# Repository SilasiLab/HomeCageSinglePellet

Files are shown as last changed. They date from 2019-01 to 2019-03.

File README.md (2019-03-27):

# **Overview**:

This system allows the user to host up to 5 mice in their home environment and automatically administer the single pellet reaching test to those animals. The system can run unsupervised and continuously for weeks at a time, allowing all 5 mice to perform an unlimited number of single pellet trials at their leisure. 

The design allows a single mouse at a time to enter the reaching tube. Upon entry, the animal’s RFID tag will be read, and if authenticated, a session will start for that animal. A session is defined as everything that happens from the time an animal enters the reaching tube to when they leave the tube. At the start of a session, the animal’s profile will be read and the task difficulty will be automatically adjusted by moving the pellet presentation arm to the appropriate distance away from the reaching tube. After the difficulty is set, pellets will begin being presented with either the left or right presentation arm, depending on which arm is specified in the mouse’s profile. Pellets will continue to be presented periodically until the mouse leaves the tube, at which point the session will end. Video and other data is recorded for the duration of each session. At session end, all the data for the session is saved in an organized way. 

# **Dependencies:**
* Ubuntu v16.04 LTS: Kernel version 4.4.19-35 or later
* Python v3.5.2
	* pySerial	
	* numpy
	* OpenCV v3.4.x
	* tkinter 
	* matplotlib
	* Pillow
	* tqdm
* Flir Spinnaker SDK v1.10.31
	* libavcodec-ffmpeg56
	* libavformat-ffmpeg56
	* libswscale-ffmpeg3
	* libswresample-ffmpeg1
	* libavutil-ffmpeg54
	* libgtkmm-2.4-dev
	* libusb-1.0-0
	
	Note: The Spinnaker dependencies are installed via official Spinnaker SDK install script.
* Arduino IDE v1.8.5

# **Software Installation:**
1. Install Ubuntu 16.04 LTS on your machine.
2. Install Anaconda. (https://www.anaconda.com/distribution/)
3. Install the Flir Spinnaker SDK v1.10.31 **INSERT GOOGLE DRIVE LINK TO SPINNAKER SDK HERE**
4. Install Arduino IDE v1.8.5. (https://www.arduino.cc/en/Main/Software)
5. Install OpenCV for C++.
	- `sudo apt-get install build-essential cmake git libgtk2.0-dev pkg-config libavcodec-dev libavformat-dev libswscale-dev`
	- `sudo apt-get install libjpeg-dev libpng-dev libtiff5-dev libjasper-dev libdc1394-22-dev libeigen3-dev libtheora-dev 			libvorbis-dev libxvidcore-dev libx264-dev sphinx-common libtbb-dev yasm libfaac-dev libopencore-amrnb-dev 			libopencore-amrwb-dev libopenexr-dev libgstreamer-plugins-base1.0-dev libavutil-dev libavfilter-dev 				libavresample-dev`
	- `sudo -s`
	- `cd /opt`
	- Download OpenCV source from https://github.com/opencv/opencv/releases/tag/3.4.4 and unpack it into /opt
	- Download OpenCV_contrib source from https://github.com/opencv/opencv_contrib/releases/3.4.4 and unpack it into /opt
	- `cd opencv`
	- `mkdir release`
	- `cd release`
	- `cmake -D BUILD_TIFF=ON -D WITH_CUDA=OFF -D ENABLE_AVX=OFF -D WITH_OPENGL=OFF -D WITH_OPENCL=OFF -D WITH_IPP=OFF -D 			WITH_TBB=ON -D BUILD_TBB=ON -D WITH_EIGEN=OFF -D WITH_V4L=OFF -D WITH_VTK=OFF -D BUILD_TESTS=OFF -D 				BUILD_PERF_TESTS=OFF -D CMAKE_BUILD_TYPE=RELEASE -D CMAKE_INSTALL_PREFIX=/usr/local -D 						OPENCV_EXTRA_MODULES_PATH=/opt/opencv_contrib/modules /opt/opencv/`
	- `make j4`
	- `make install`
	- `ldconfig`
	- `exit`
	- `cd`
	- `pkg-config --modversion opencv`
	- If everything worked correctly, output should read "3.4.4".
	
5. Create and configure a virtual environment for installing the HomeCageSinglePellet code.
	- `conda create -n <yourenvname> python=3.5.2 anaconda`
	- `conda activate <yourenvname>`
	- `conda install -c conda-forge opencv=3.4.4`
	- `conda install -c anaconda numpy`
	- `conda install -c anaconda pyserial`
	- `conda install -c anaconda tk`
	- `conda install -c conda-forge matplotlib`
	- `conda install tqdm`
	- `conda install Pillow`

6. Download the HCSP source code from https://github.com/SilasiLab/HomeCageSinglePellet and unpack it.
7. Optional (Only if you want to use the analysis features): Install Deeplabcut using the Anaconda based pip installation method. (https://github.com/AlexEMG/DeepLabCut/blob/master/docs/installation.md)
8. Optional (Only if you want to use the anaylsis features): Move the file `HomeCageSinglePellet/src/analysis/HCSP_analyze.py` into `~/.conda/envs/DLC2/lib/python3.6/site-packages/deeplabcut` (Where DLC2 is the name of the anaconda virtual environment where you installed Deeplabcut).
9. Optional (Only if you want to use the anaylsis features): Download our pretrained DLC2 network for automatically extracting reach attempts from your videos. **INSERT GOOGLE DRIVE LINK TO NETWORK HERE**
8. Done!

# **Assembly:**

### **Prerequisites:**

1. Obtain all the parts listed in `HomeCageSinglePellet/resources/partsList.xls`
2. Have the PCB `HomeCageSinglePellet/resources/PCB/nano.brd` manufactured (Find a manufacturer, send them the .brd file using
whatever process they use for upload, wait for it in the mail).
3. 3D print all the .stl files contained in `HomeCageSinglePellet/resources/CAD/STL/`

### **Attach headers and components to the PCB**

1. Attach female headers for the Arduino onto the PCB. Attach male headers onto the CAMTRIG, MSZ, SERVO1, SERVO2, RFID and
IRBREAK holes on the PCB.
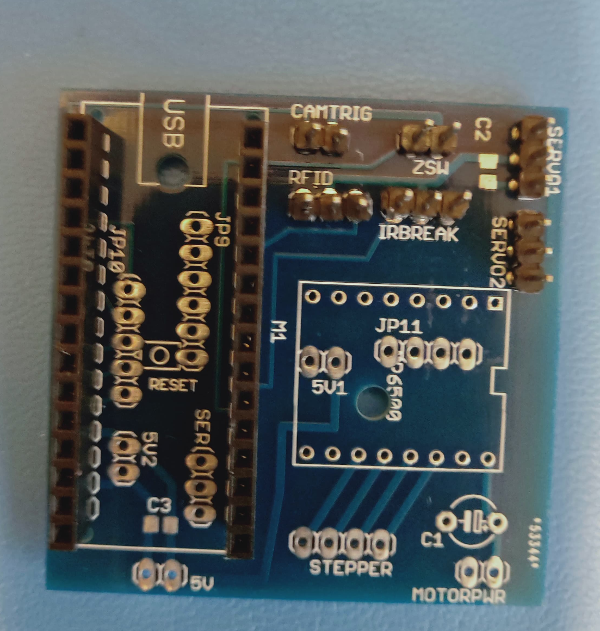
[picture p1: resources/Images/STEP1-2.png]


2. Solder the stepper driver to the PCB in the orientation shown in the picture. (Note that the holes on 
the PCB are spaced too far apart for the stepper driver pins). To address this we bend the pins of the driver to fit. You'll 
need to do this until someone gets around to fixing the PCB layout.

	
3. Solder the capacitor across C1 as shown in the picture. (TODO: INSERT PICTURE)

### **Install the voltage regulator and power connectors**

4. Voltage regulator output must be set to 5V by turning the small screw on the blue pot. This is done my powering the device with 12V and recording the output with multimeter while adjusting the pot screw.
Attach 6 leads to the voltage regulator:
	- 2 Leads to the positive input pad.
	- 2 leads to the negative input pad.
	- 1 lead to the positive output pad.
	- 1 lead to the negative output pad.


	
5. Short the neutral and ground leads on the circular power connectors by soldering a small wire across them.


6. Line up the voltage regulator in the box and drill holes through the box where you want to mount the regulator.


7. Screw one of the circular power connectors into the bottom hole.


8. Solder one of the negative input leads you attached to the voltage regulator in step 1 onto the negative lead of the 
power connector you screwed in in step 4.


9. Solder one of the positive input leads you attached to the voltage regulator in step 1 onto the positive lead of the
power connector you screwed in in step 4. 


10. Place the PCB into the box and drill holes into the box where the mount holes on the PCB line up. 
Then mount the PCB with some bolts. Metal bolts are fine, they won't touch anything that will be a problem. 
Use nylon washers if you're nervous.


11. Solder the remaining positive input power lead that you attached to the voltage regulator in 
step 5 to the positive MOTORPWR pad on the PCB.


12. Solder the remaining negative input power lead that you attached to the voltage regulator in 
step 5 to the negative MOTORPWR pad on the PCB.
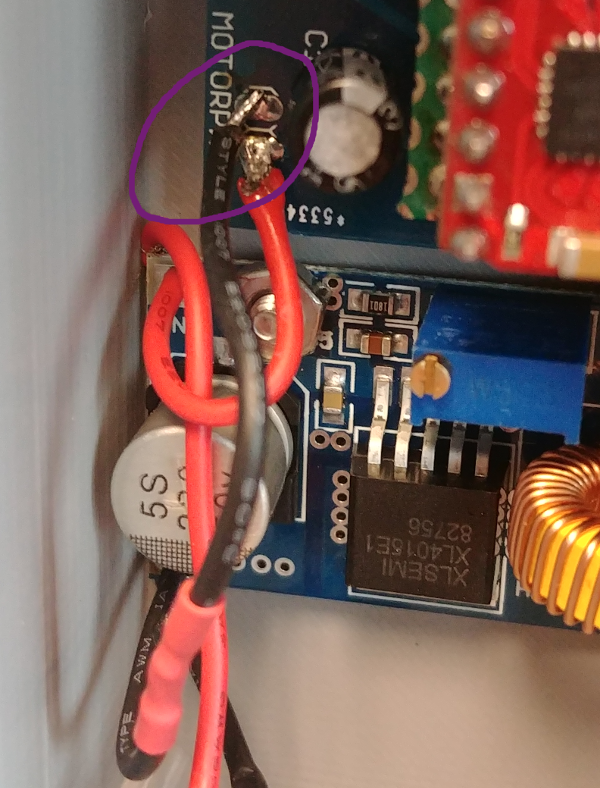
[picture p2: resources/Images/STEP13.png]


13. Screw in the second circular power connector to the remaining hole in the box. Solder a wire from the negative lead of the
second power connector to the negative lead of the first power connctor. Solder a wire from the positive lead of the second power
connector to the positive lead of the first power connector.
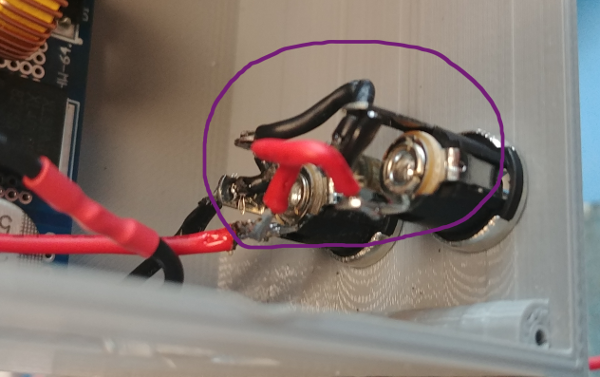
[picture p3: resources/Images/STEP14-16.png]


### **Assemble the pellet delivery system and mouse tube**

14. Line the hopper rail piece up on the baseplate and screw in the 4 screws that hold it in place.


15. Attach the stepper motor as shown in the picture. Attach the coupler to the shaft of the motor. **Note:** For the steps involving the stepper motor, coupler and coupling screw; We don't yet have a design that uses standard parts. We currently take the screw detailed in the parts list and cut it and the stepper motor shaft to the correct lenght. **INSERT CORRECT LENGTH OF STEPPER MOTOR SHAFT AND COUPLING SCREW HERE.**

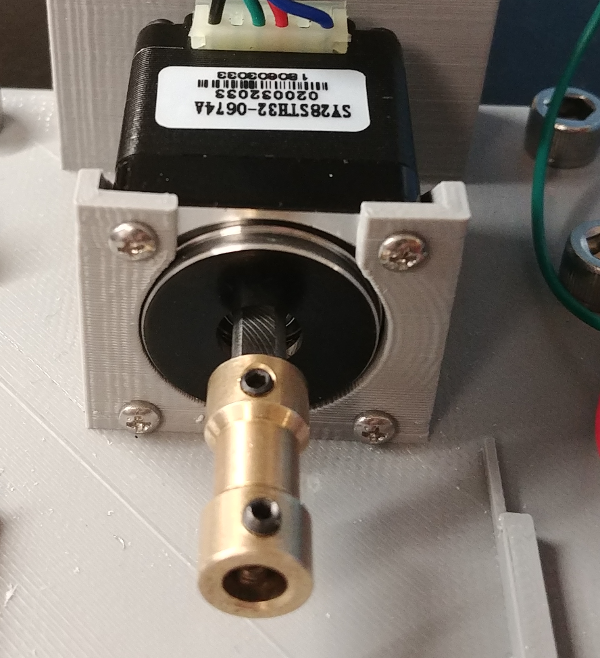
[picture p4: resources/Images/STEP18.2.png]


16. Attach the screw to the stepper coupler. Slide the hopper onto the rails and insert the nut into the slot where the stepper coupler screw will go. Then thread the shaft coming out of the coupler into the nut. 
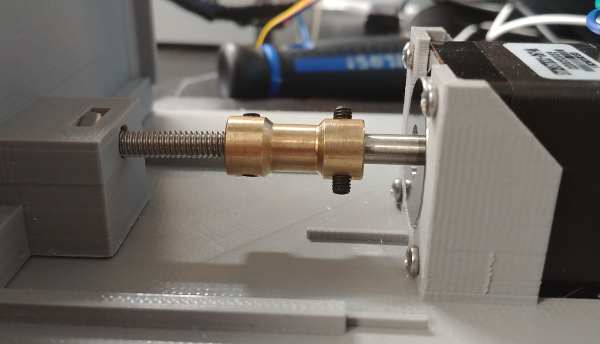
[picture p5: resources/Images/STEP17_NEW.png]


17. Rotate the stepper coupler until the screw is all the way into the hopper nut. Solder two leads to the microswitch,
one each on the left and right prongs coming out of the switch. Use superglue to glue the microswitch down so it will be pressed
when the hopper reaches it's closest point to the motor. 
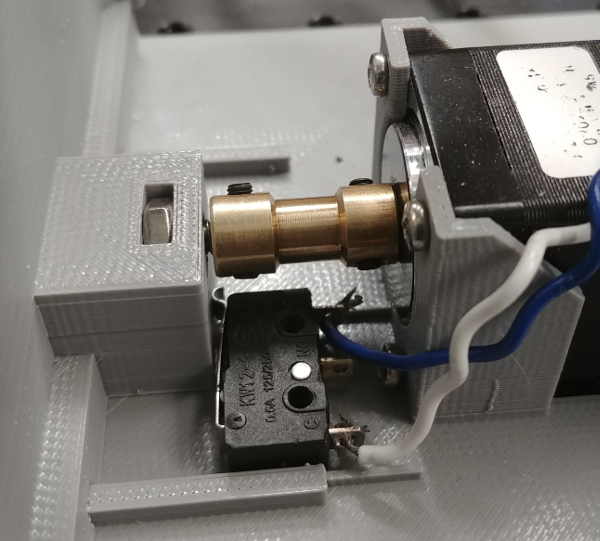
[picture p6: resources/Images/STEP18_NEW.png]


18. Attach both front surface mirrors to the mirror mount piece with double sided tape.


19. Slide the front-wall/mirror holder piece over the end of the acrylic tube.


20. Use your favorite adhesive to attach the IR-Breaker to the IR-Breaker holder.
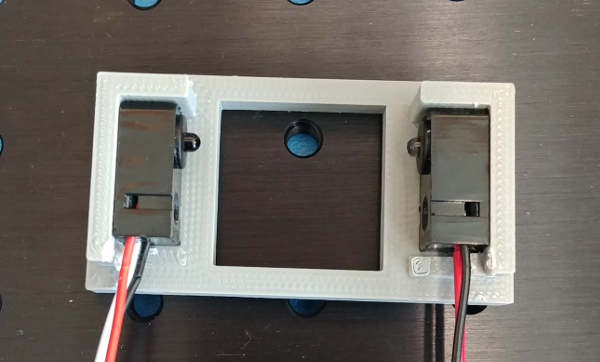
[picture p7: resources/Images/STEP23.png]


21. Slide the IR-Breaker holder over the tube so that the beam runs across the bottom of the tube 
(Where the mice feet will be).
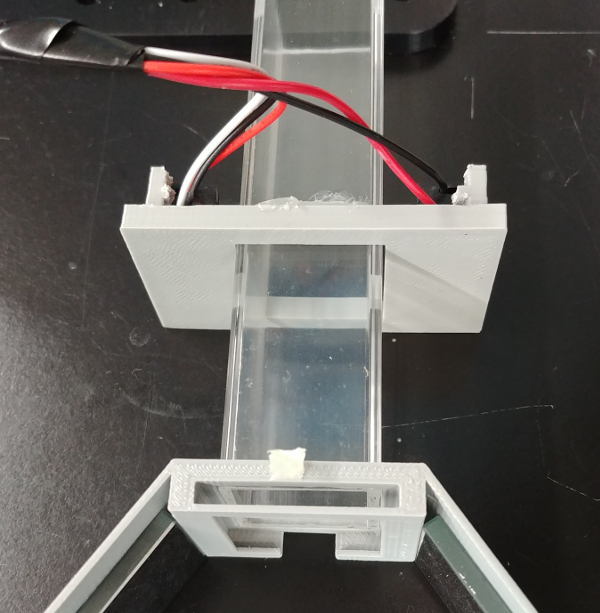
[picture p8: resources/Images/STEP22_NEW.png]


22. Hotglue the RFID reader to the acrylic tube as shown.(Note: Push the IR-Breaker holder up against the RFID module so that 
it's sandwiched between the IR-Breaker holder and the front-wall/mirror holder, and hot glue it all in place).


23. Slot the assembled acrylic tube into the square hole on the rail baseplate mount as shown.


24. Line up both servos as shown in the picture. Rotate the servo splines as far as they will go in the 
directions shown in the picture.


25. Use an allen key to insert the set screws into the tips of the hopper arms.
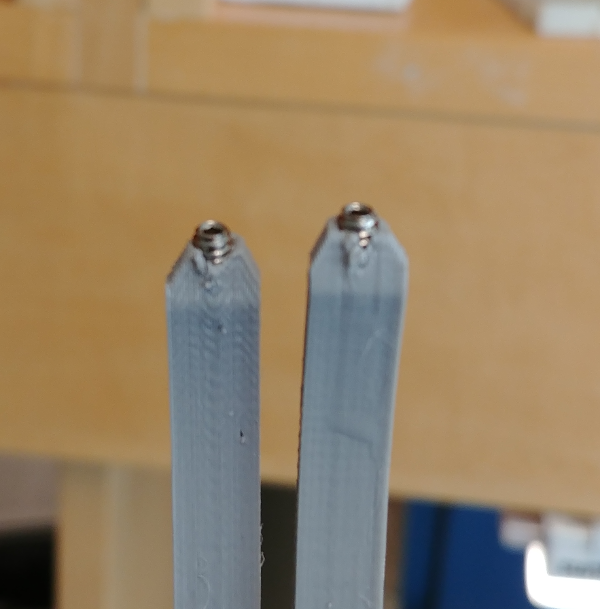
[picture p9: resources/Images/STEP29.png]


26. Attach the hopper arms to the servo spline as shown in the picture. (Note: This is why we 
rotated the servo spline as far as possible in step 28, so that you can set the maximum retraction 
point of the hopper arms by attaching them how you like).


27. Line the servos with attached hopper arms up as shown in the picture and use your favourite adhesive to 
adhere them to the servo mount points on the hopper. **Note:** This step can be finicky. Before you adhere the servos to the 
hopper, ensure the hopper arms will rotate easily at their pivot point and that they slide easily through the holes in the 
hopper. If there is too much friction the arms will vibrate and jump around as they move, and since their function is to 
balance millet seeds on a small set screw, vibrations are bad.


28. This step is where we will glue the acrylic tube permanently into the sqaure 3D printed hole it sits in. Rotate the stepper
coupler until the hopper is as close as it can get to the motor. Now rotate the hopper arms up so that they are sitting infront 
of the tube opening as shown. On bootup the stepper motor will "zero" the hopper using the limit switch. We want this zero point
to put our pellet presentation arms directly infront of the tube opening. Additionally we want the tube to sit at a high enough angle that the hopper will not catch on the mirrors or any part of the tube assembly when it moves. Once you're satisfied that both these requirements are met, glue the tube into place. 
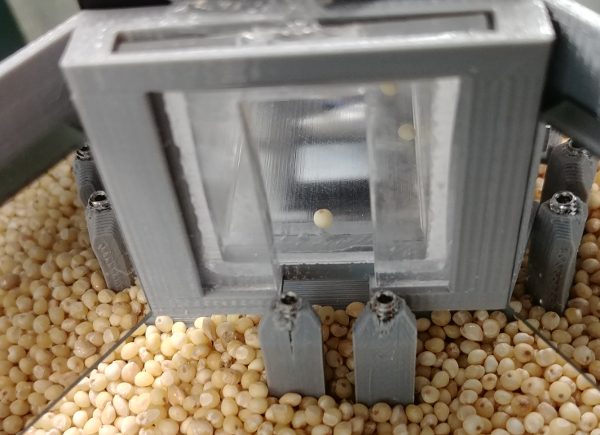
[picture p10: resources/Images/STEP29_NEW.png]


29. Splice the power wires of both servo motors together. Splice the ground wires of both servo motors together. Splice the servo power wire into the lead coming out of the voltage regulator positive output. Splice the servo ground wire into the lead coming out of the voltage regulator negative output.
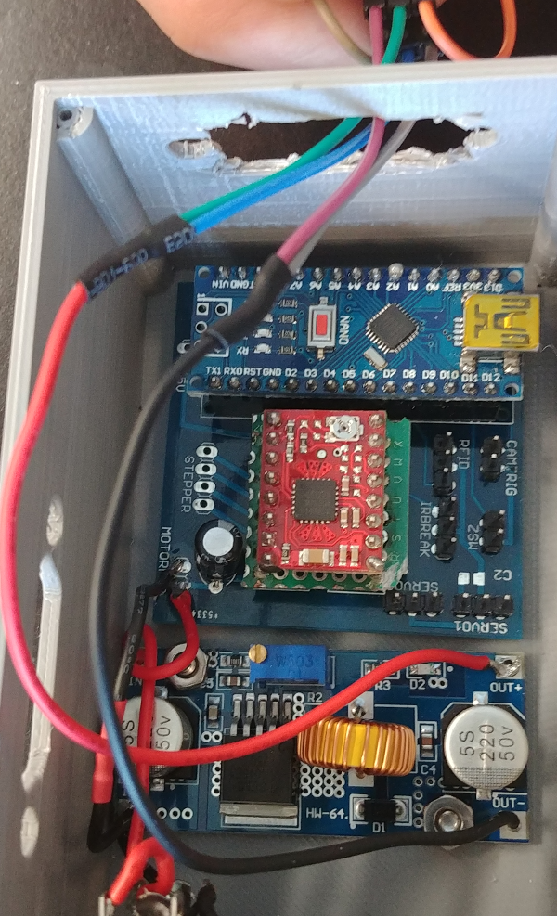
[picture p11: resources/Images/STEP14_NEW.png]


30. Plug the leftmost servo signal wire into the SERV02 signal pin on the PCB. Plug the rightmost servo signal wire into the 
SERVO1 signal pin on the PCB.
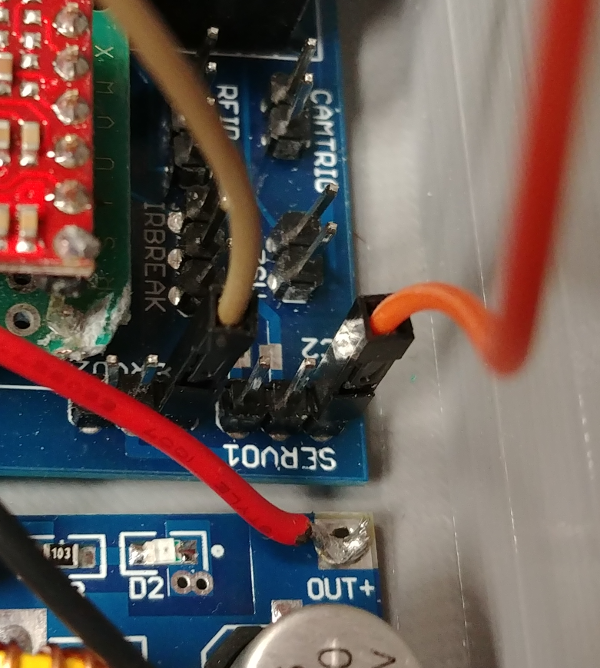
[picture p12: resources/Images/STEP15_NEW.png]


31. Splice the power wires of the IRbreak LED and photo diode together. Splice the ground wires of the IRBreak LED and photo diode together. Plug the spliced power, spliced ground and signal line of the IRbreaker into the IRBREAK pins on the PCB. 
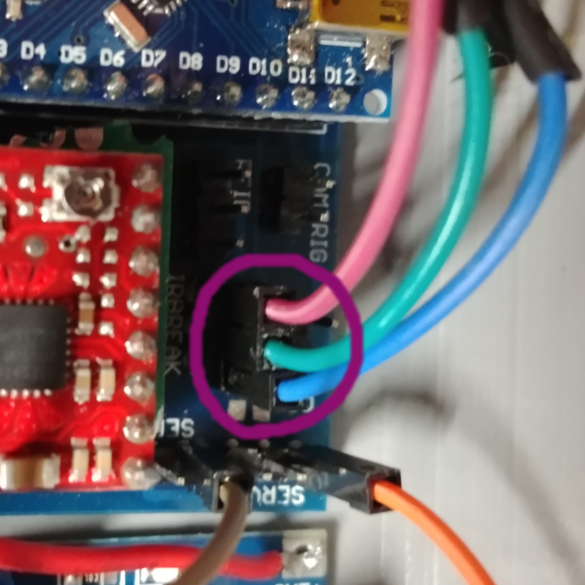
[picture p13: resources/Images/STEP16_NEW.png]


32. Plug the microswitch wires into the MSZ pins on the PCB. (TODO: Figure out which wire goes onto which pin and add a picture)

33. Plug the 12V 1A power supply into either of the circulaer power connectors on the PCB box.

34. Plug one of the micro USB cables into the Arduino on one end and the PC on the other.

35. Plug one of the micro USB cables into the Arduino on one end and the PC on the other.

36. Assembly complete!
 
# **Calibration and Configuration:**

1. You'll need to upload the `HomeCageSinglePellet/src/arduino/homecage_server/homecage_server.ino` file to the Arduino. 
(https://www.arduino.cc/en/Guide/ArduinoNano)
NB.:
* A. After a fresh install of Ubuntu, there may be issues accessing serial ports. Run the following command to give full access: sudo usermod -a -G dialout $USER  (in our case user: silasi).
* B. Use following setting in Arduino IDE: 
	- 1. Tools -> Board -> Arduino Nano
	- 2. Tools -> Processor -> Atmega 328P (Old Bootloader)
2. There are 4 constants that will need to be modified in the file
`HomeCageSinglePellet/src/arduino/homecage_server/homecage_server.ino`
They are: `SERVO1_UP_POS`, `SERVO1_DOWN_POS`, `SERVO2_UP_POS` and `SERVO2_DOWN_POS`. They are located
on lines 41,43,45 and 47 respectively. These constants represent the PWM signal going to each servo. I won't explain PWM here,
all you need to know is different numbers correspond to different positions for the servos. In the main loop, lines 421-425 
have a block that will make the arms go up and down one at a time in an infinite loop. You'll need to observe the up/down 
positions of the arms during these movements to dial in the correct position, using the constants mentioned above. I haven't 
found a better way to do this yet, and frankly all the arduino code is poorly written. Any improvements or a rewrite would be 
welcomed. Once you're happy with the up/down position of each arm during their "pellet presenting" movements, comment 
the infinite loop out and upload to the Arduino.
	
2. Open `HomeCageSinglePellet/config/config.txt` and set the path to your `HomeCageSinglePellet/AnimalProfiles/` 
directory. (One of the Spinnaker video writing functions doesn't work with relative paths so we chose to work with 
full paths). I believe python has a library that will turn a relative path into a full path, so this could be fixed in 
the future.
	
3. We don't provide exact details on camera setup, but if you want to use the analysis features provided in this 
project, it will be important to have video recording conditions as close as possible to ours. The performance of 
deelabcut will degrade rapidly as conditions stray from those used to produce the frames used to train the network.
Additionally the functions in kinalyze.py are dependent on specific recording conditions. If you plan to use the analysis 
features, leave the recording settings in `HomeCageSinglePellet/config/config.txt` as the default. In terms of lighting 
conditions, camera mounting, recording angle, etc, just do your best to make it look like the picture below. If it's close 
enough, the analysis pipeline will work. **INSERT PICTURE OF FRAME CAPTURED BY PTGREY**

# **Usage**:
### **Running the Device**
1. Enter the virtual environment that the system was installed in by typing `source activate <my_env>` into a terminal.

2. Use `cd` to navigate to HomeCageSinglePellet/src/client/ and then run `python -B genProfiles.py`. The text prompts will walk you through entering your new animals into the system.

3. Open HomeCageSinglePellet/config/config.txt and set the system configuration you want.

4. Enter HomeCageSinglePellet/src/client/ and run `python -B main.py`

5. To test that everything is running correctly, block the IR beam breaker with something
	and scan one of the system’s test tags. If a session starts properly, it’s working.

6. To shut the system down cleanly; 

	- Ensure no sessions are currently running. 
	- Press the quit button on the GUI.
	- Ctrl+c out of the program running in the terminal.
NB.
1. Arduino needs to be USB0 , and RFID reader needs to be USB1. You can see connected USB devices with terminal command:
ls /dev/tty*

### **Analysis**:

A high level analysis script is provided that runs the data for all animals through a long analysis pipeline. The functions performed on each video include;

* Analyze with Deeplabcut2.
* Identify all reaching attempts and record frame indexes where reaches occur.
* Compute 3D trajectory of reaches and estimate magnitude of movement in millimeters.
* Cut videos to remove any footage not within the bounds of a reaching event.
* Neatly package data for each analyzed video in a descriptively named folder within the animals ./Analyses/ directory.



This analysis is started by entering the HomeCageSinglePellet/src/analysis/ directory and running
`bash analyze_videos.sh <CONFIG_PATH> <VIDEO_DIRECTORY> <NETWORK_NAME>`

This script takes the following input;

**CONFIG_PATH** = Full path to config.yaml file in root directory of DLC2 project.
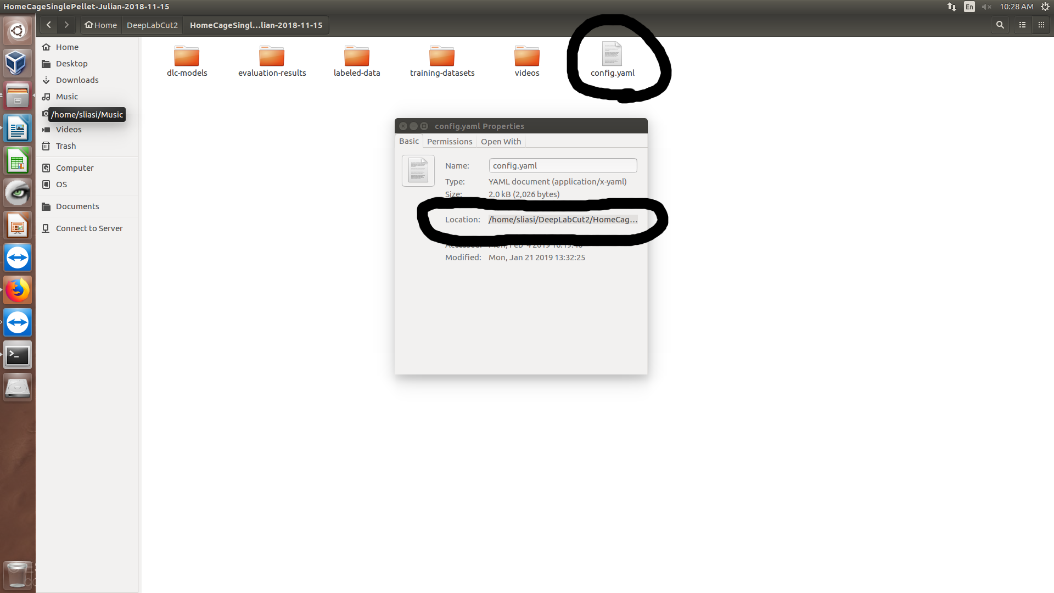
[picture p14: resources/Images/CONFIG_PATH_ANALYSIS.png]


**VIDEO_DIRECTORY** = Full path to directory containing videos you want to analyze. (e.g <~/HomeCageSinglePellet/AnimalProfiles/MOUSE1/Videos/>)

**NETWORK_NAME** = Full name of DLC2 network you want to use to analyze videos. (e.g <DeepCut_res
net50_HomeCageSinglePelletNov18shuffle1_950000>)

Another script (`HomeCageSinglePellet/src/analysis/scoreTrials.py`) is provided for manually categorizing reaches once they have been identified in the step detailed above. This script opens a GUI that allows the user to select an animal and browse through all the videos that have been analyzed for that animal. (In the video list, blue videos indicate videos where reaches were detected by the analysis software. Beige videos indicate videos where no reaches were detected. Green videos indicate videos that have already been manually scored). When users select a video from the list, the video window will display the first detected reach in a loop. It will also display the "reach count" (e.g 1/16) to indicate how many reaches the video contains and which one is currently being viewed. The user can then use the mouse or a hotkey to place the current reach into a category. The video window will then jump to the next reach. This repeats until all the reaches for a given video are scored, at which point the category information will be saved. 
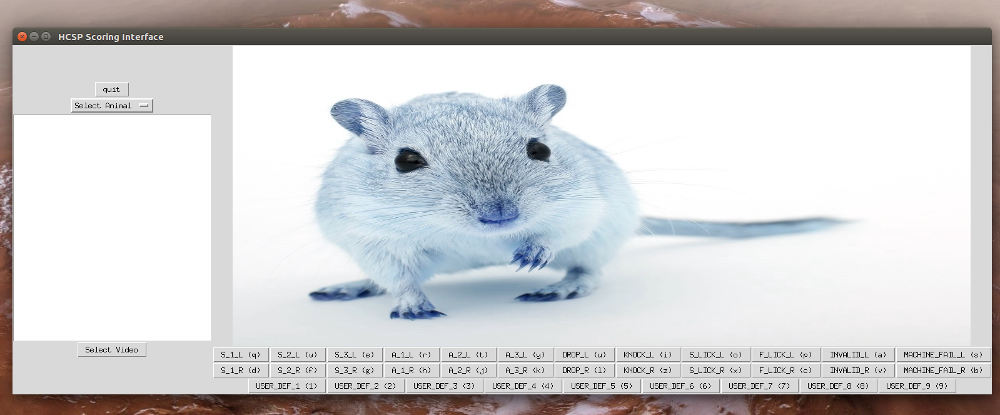
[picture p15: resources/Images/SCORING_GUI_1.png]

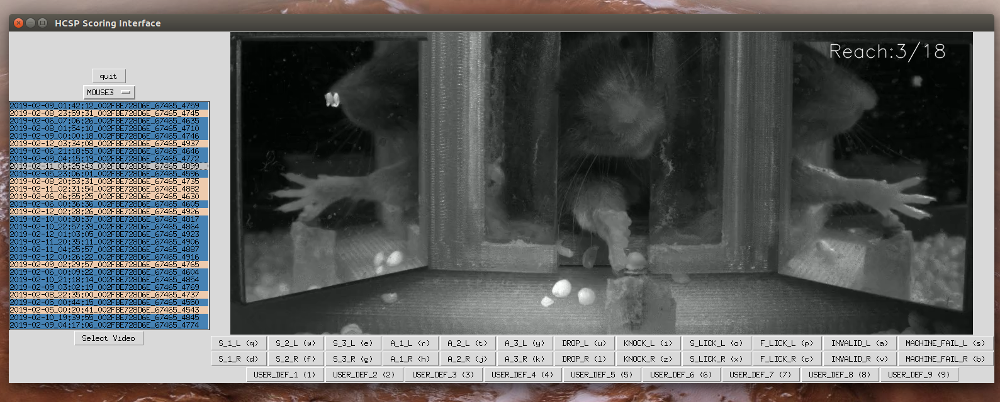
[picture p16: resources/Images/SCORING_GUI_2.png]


**Note:** All the analysis functions read and write all their data to/from `HomeCageSinglePellet/AnimalProfiles/<animal_name>/Analyses/`. Information for each video is saved in a unique folder whose name includes video creation date, animal RFID, cage number and session number. (e.g `2019-01-25_14:36:31_002FBE737B99_67465_5233`). Each of these folders will contain the raw video, the deeplabcut output from analyzing the video (.h5 and .csv formats). In addition, if >=1 reaches were found in the video, the folder will contain a file named date_time_rfid_cage_number_session_number_reaches.txt (e.g `2019-01-25_14:36:31_002FBE737B99_67465_5233_reaches.txt`). This file contains the start and stop frame indexes of each reach in the video and (x,y,z) vectors for each reach. In addition, once a video has been scored manually using `scoreTrials.py`, a file named date_time_rfid_cage_number_session_number_reaches_scored.txt (e.g `2019-01-25_14:36:31_002FBE737B99_67465_5233_reaches_scored.txt`) will be added to the video's folder. This file is the same as date_time_rfid_cage_number_session_number_reaches.txt, except that it also contains a category identifier for every reach.

# **Troubleshooting**:

* Is everything plugged in?
* Shutting the system down incorrectly will often cause the camera and camera software to enter a bad state.
	* Check if the light on the camera is solid green. If it is, unplug the camera and plug it back in.
	* Check the HomeCageSinglePellet/src/client/ directory for a file named KILL. If this file exists, delete it.
	* Make sure the camera is plugged into a USB 3.0 or greater port and that it is not sharing a USB bridge with too many 			other devices (I.e if you have 43 devices plugged into the back of the computer and none in the front, plug the 		camera into the front).
* Make sure you are in the correct virtual environment.
* Make sure the HomeCageSinglePellet/config/config.txt file contains the correct configuration. (If the file gets deleted it will be replaced by a default version at system start)
* Make sure there are 1 to 5 profiles in the HomeCageSinglePellet/AnimalProfiles/ directory. Ensure these profiles contain all 		the appropriate files and that the save.txt file for each animal contains the correct information. 
* Make sure that the Arduino mounted as device ttyUSB0 and that the RFID reader mounted as ttyUSB1 in /dev/. If they mounted 
differently, rebooting and attaching them in the correct order will fix the problem.

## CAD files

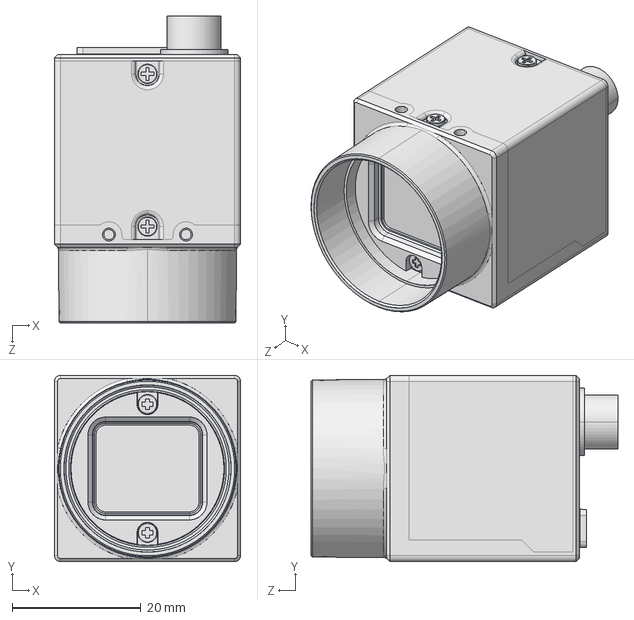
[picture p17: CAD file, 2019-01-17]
resources/CAD/Flir/FL2-020-R0.IGS
29.0 x 29.0 x 47.8 mm

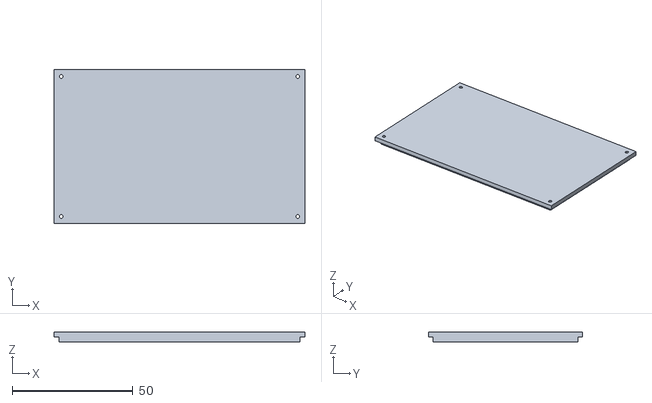
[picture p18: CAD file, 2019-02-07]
resources/CAD/STL/PCB_lib.stl
104.0 x 64.0 x 4.00

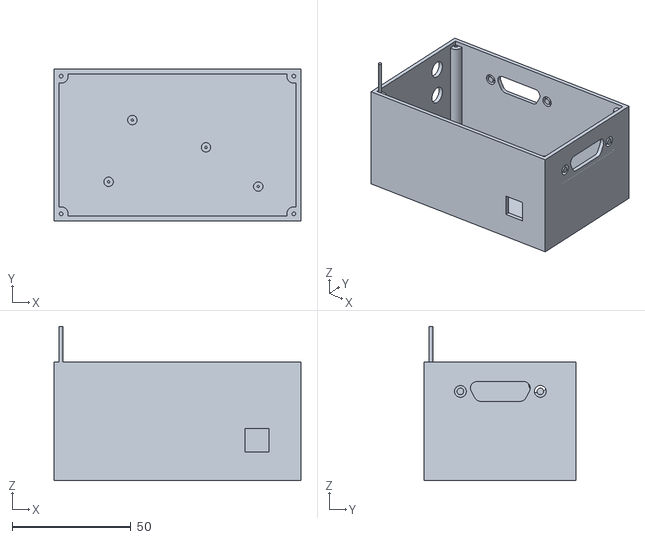
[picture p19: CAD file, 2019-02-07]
resources/CAD/STL/PCB_box.stl
104.0 x 64.0 x 65.0

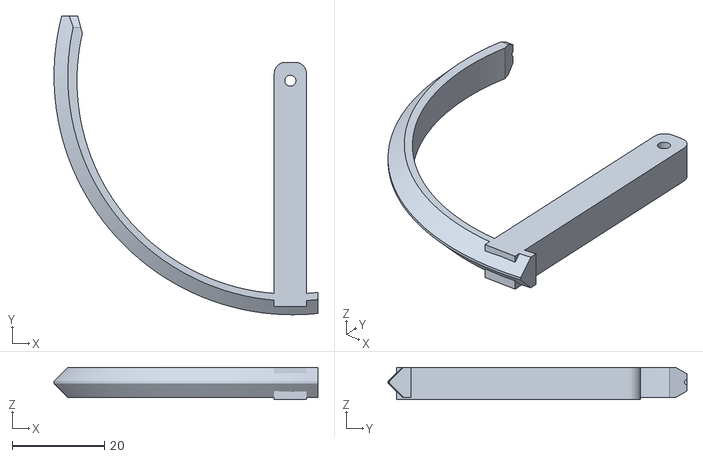
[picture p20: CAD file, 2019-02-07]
resources/CAD/STL/hopper_arm_right.stl
57.3 x 64.8 x 7.00

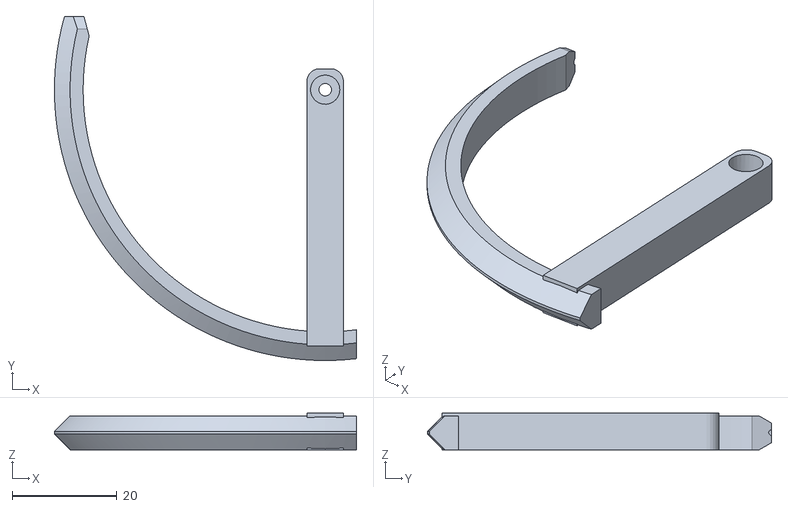
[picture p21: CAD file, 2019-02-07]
resources/CAD/STL/hopper_arm_left.stl
57.8 x 65.8 x 7.00

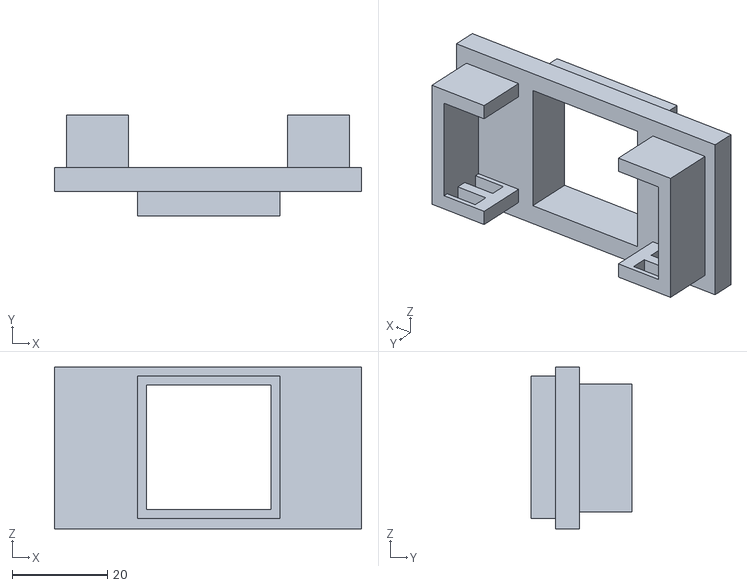
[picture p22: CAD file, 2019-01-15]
resources/CAD/STL/beam_breaker_mount.stl
64.5 x 21.2 x 34.0

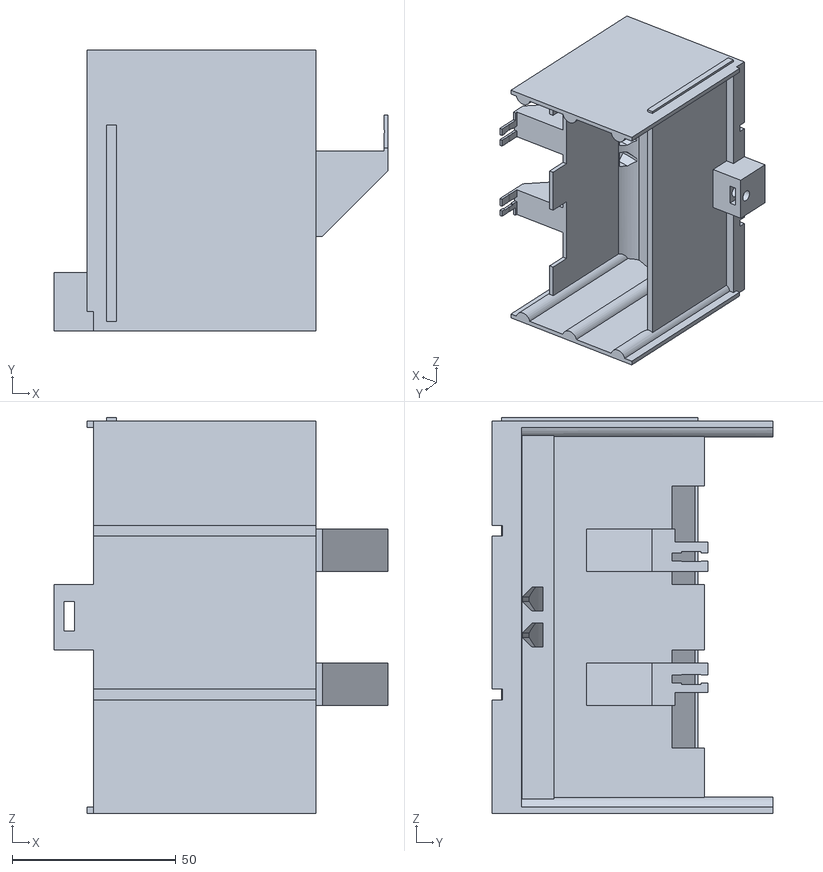
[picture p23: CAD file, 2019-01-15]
resources/CAD/STL/hopper.stl
102.0 x 86.0 x 121.0

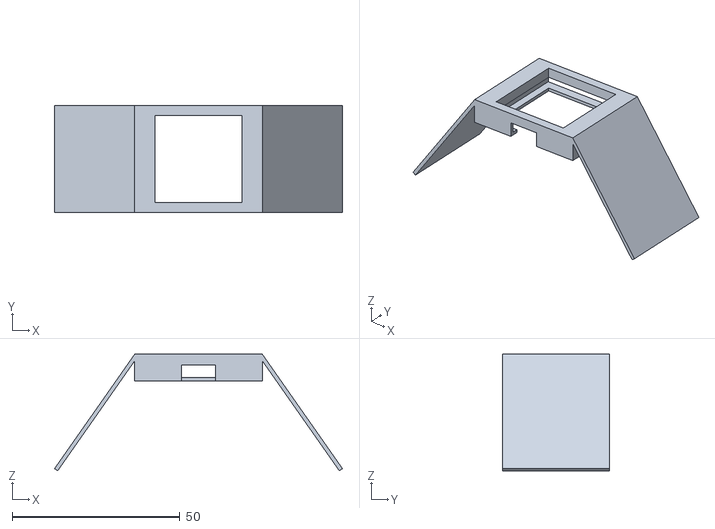
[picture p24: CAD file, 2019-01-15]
resources/CAD/STL/frontwall_mirror_mount.stl
85.8 x 32.0 x 34.8

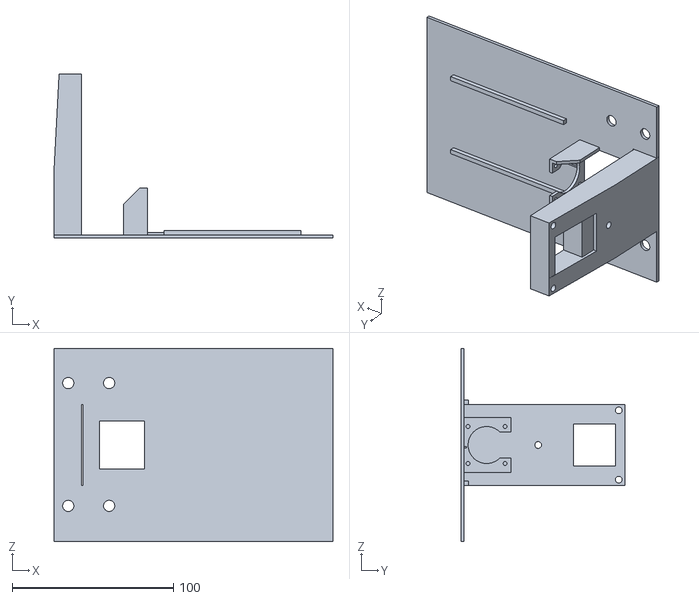
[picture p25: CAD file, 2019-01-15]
resources/CAD/STL/baseplate.stl
173.1 x 102.0 x 120.0

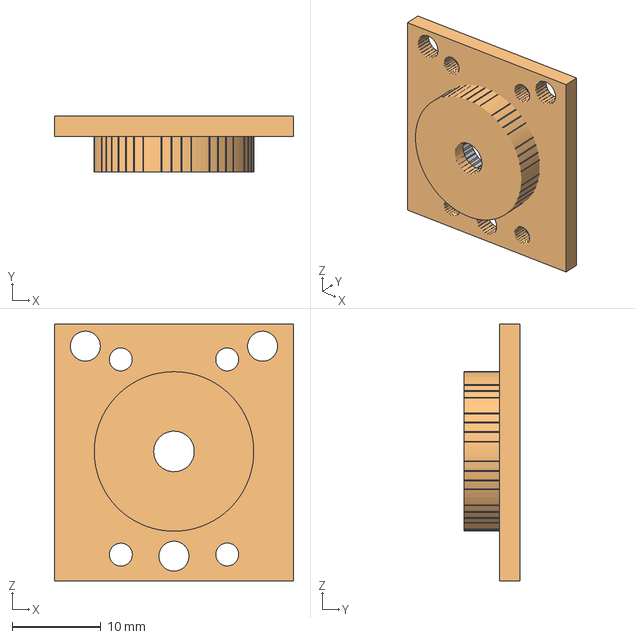
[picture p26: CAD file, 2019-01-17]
resources/CAD/FreeCAD/Flir_BlackflyS_ThorLabs_post_mount.fcstd
27.0 x 6.27 x 29.0 mm
Pocket003 (Meshed)

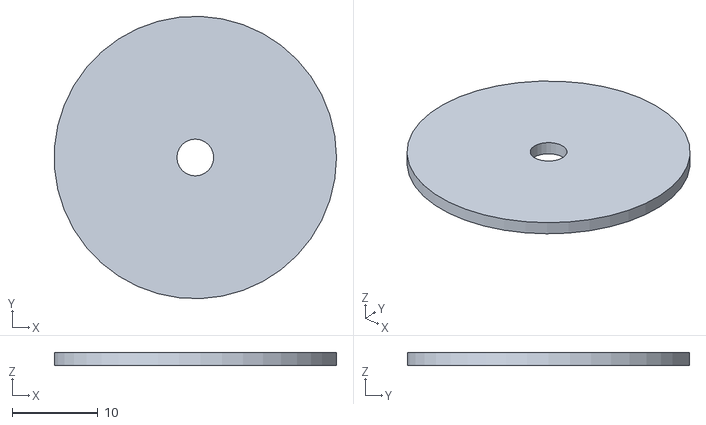
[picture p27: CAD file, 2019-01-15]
resources/CAD/STL/IR_ringlight_ThorLabs_post_mount.stl
33.0 x 33.0 x 1.50

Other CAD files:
resources/CAD/STL/Flir_BlackflyS_ThorLabs_post_mount.stl

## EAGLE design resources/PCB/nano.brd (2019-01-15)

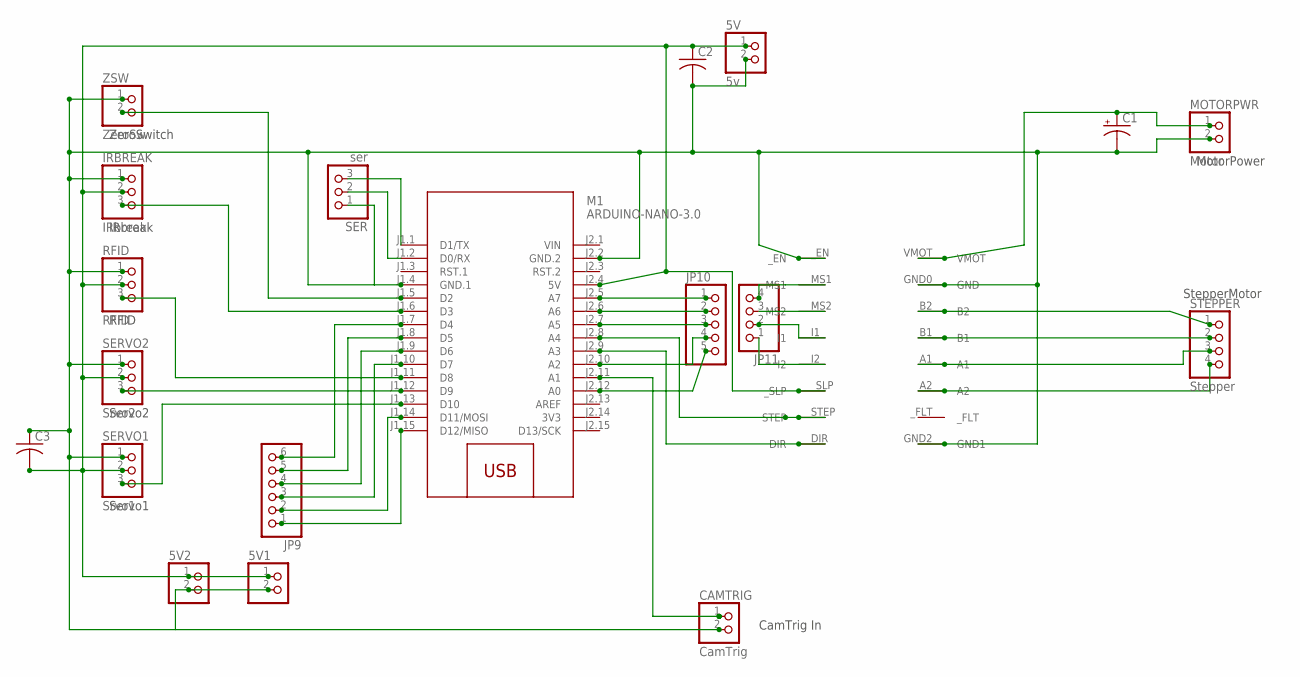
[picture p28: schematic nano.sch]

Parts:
5V: 5v; 1X02
5V1, 5V2: PINHD-1X2; 1X02
C1: CPOL-USE5-5; E5-5
C2, C3: C-USC0805; C0805
CAMTRIG: CamTrig; 1X02
IRBREAK: IRbreak; 1X03
JP9: PINHD-1X6; 1X06
JP10: PINHD-1X5; 1X05
JP11: PINHD-1X4; 1X04
M1: ARDUINO-NANO-3.0
MOTORPWR: Motor; 1X02
RFID: RFID; 1X03
SER: ser; 1X03
SERVO1: Srvo1; 1X03
SERVO2: Srvo2; 1X03
STEPPER: Stepper; 1X04
U$1: MP6500
ZSW: ZeroSw; 1X02

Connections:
3V3: M1.J2.14 (3V3)
unnamed: C1.+, MOTORPWR.1, U$1.VMOT
unnamed: JP9.1, M1.J1.15 (D12/MISO)
unnamed: JP11.4, U$1.MS1
unnamed: STEPPER.4, U$1.A2
unnamed: STEPPER.3, U$1.A1
unnamed: STEPPER.2, U$1.B1
unnamed: STEPPER.1, U$1.B2
unnamed: JP9.2, M1.J1.14 (D11/MOSI)
unnamed: JP9.3, M1.J1.10 (D7)
unnamed: M1.J1.12 (D9), SERVO2.3
unnamed: M1.J1.13 (D10), SERVO1.3
unnamed: M1.J1.5 (D2), ZSW.2
unnamed: IRBREAK.3, M1.J1.6 (D3)
unnamed: M1.J1.11 (D8), RFID.3
unnamed: CAMTRIG.1, M1.J2.11 (A1)
unnamed: M1.J2.9 (A3), U$1.DIR
unnamed: M1.J2.8 (A4), U$1.STEP
unnamed: JP9.4, M1.J1.9 (D6)
unnamed: 5V.1, 5V1.1, 5V2.1, C2.1, C3.2, IRBREAK.2, M1.J2.4 (5V), RFID.2, SERVO1.2, SERVO2.2, U$1._SLP
unnamed: JP9.5, M1.J1.8 (D5)
unnamed: JP9.6, M1.J1.7 (D4)
unnamed: JP10.1, M1.J2.5 (A7)
unnamed: JP10.2, M1.J2.6 (A6)
unnamed: JP10.3, M1.J2.7 (A5)
unnamed: JP10.4, M1.J2.10 (A2)
unnamed: JP10.5, M1.J2.12 (A0)
unnamed: 5V.2, 5V1.2, 5V2.2, C1.-, C2.2, C3.1, CAMTRIG.2, IRBREAK.1, M1.J1.4 (GND.1), M1.J2.2 (GND.2), MOTORPWR.2, RFID.1, SER.1, SERVO1.1, SERVO2.1, U$1.GND0 (GND), U$1.GND2 (GND1), U$1._EN, ZSW.1
unnamed: JP11.3, U$1.MS2
unnamed: JP11.2, U$1.I1
unnamed: JP11.1, U$1.I2
unnamed: M1.J1.1 (D1/TX), SER.3
unnamed: M1.J1.2 (D0/RX), SER.2
VIN: M1.J2.1 (VIN)

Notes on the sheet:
Servo1
Servo2
RFID
IRbreak
ZeroSwitch
StepperMotor
MotorPower
CamTrig In

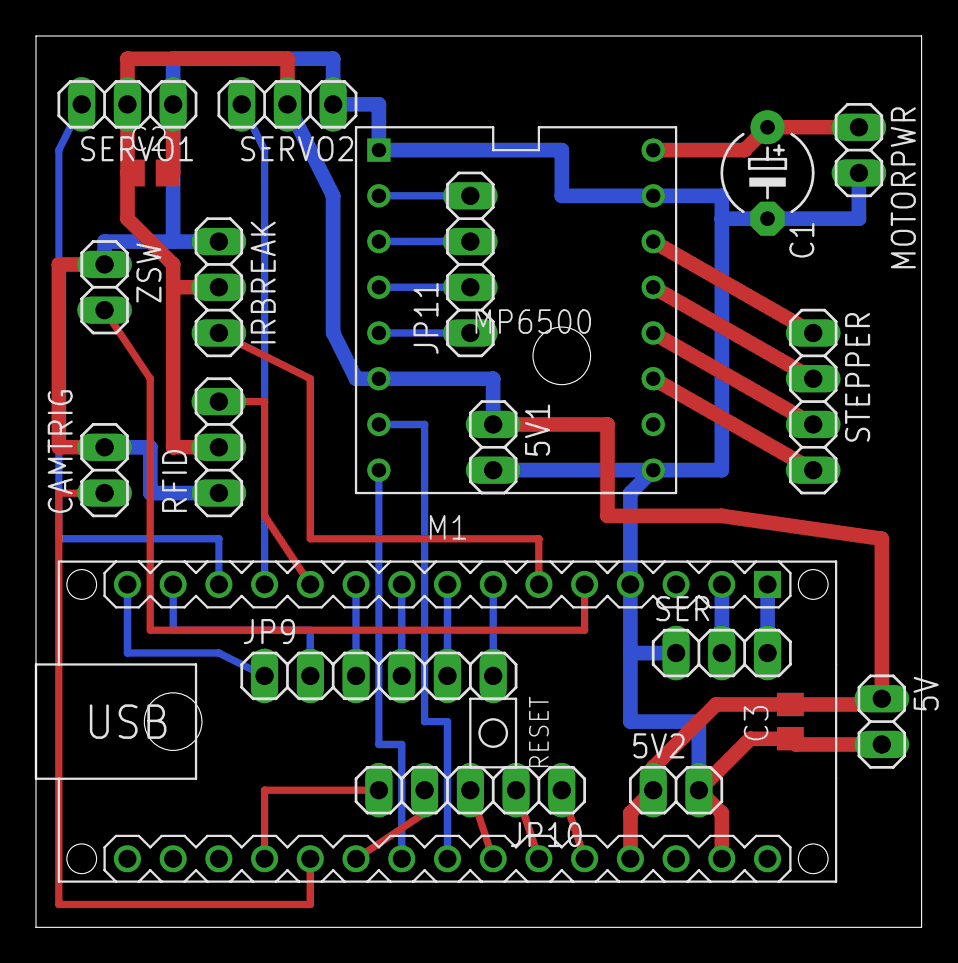
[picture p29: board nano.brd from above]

Board: 2 copper layers, 49.2 x 49.5 mm, 20 parts (0 on the bottom side), 32 nets.

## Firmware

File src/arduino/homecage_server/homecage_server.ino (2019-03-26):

/*
    This program is a server for controlling the hardware peripherals attached to the HomeCage system.
    It waits for commands over a serial port (python client in our case) and performs the desired action upon receiving the command.
    There is no proper message passing system and it simply uses various magic byte values as messages.
    Note: These bytes can cause different outcomes depending on the state the program is in at the time
    of receiving. The lack of real message passing system means the program is rather fragile. I recommend
    not modifying this program too much. Utility may instead be found by recycling specific functions.
    (For controlling servos, steppers, IR breakers, etc....attached to the Arduino).


    This program enters a listening mode on boot and waits for a signal over serial to tell it to start a session.
    Once this signal is received, the program expects to receive a byte value representing how far the stepper should
    rotate from the origin (The origin is defined on start-up by retracting the stepper motor until the limit switch
    is pressed). After the stepper motor is positioned, the program expects to receive repeating requests for
    pellet presentations (with either arm). The program continues in this state until the IR breaker is connected.
    At this point the server sends a session termination message to the client and tears the session down, re-entering
    it's default listening mode.


    Author: Julian Pitney
    Email: JulianPitney@gmail.com
    Organization: University of Ottawa (Silasi Lab)

*/





#include <Servo.h>

// Config
const int servo1Pin = 10;
const int servo2Pin = 9;
Servo servo1;
Servo servo2;
bool servo1_up_flag = false;
bool servo2_up_flag = false;
const int SERVO_SETTLE_DELAY = 300;
// Higher numbers make the arm go higher
int SERVO1_UP_POS = 72;
// Low numbers makehe arm go lower
int SERVO1_DOWN_POS = 140;
// Lower numbers make the arm go higher
int SERVO2_UP_POS = 110;
// High numbers make the arm go lower
int SERVO2_DOWN_POS = 45;
int SERVO_PULSE_DELAY = 16;
int servo1Pos = SERVO1_DOWN_POS;
int servo2Pos = SERVO2_DOWN_POS;
typedef enum {left,right} whichServo;

const int ledPin = 13;
const int switchPin = 2;
const int IRBreakerPin = 3;
const int ptgreyGPIOSignalPin = A1;

volatile byte switchState = digitalRead(switchPin);
volatile byte IRState;

int stepperDistFromOrigin = -1;
double stepsToMmRatio = 420;


// Hardware interrupt handler for switch pin
void handleSwitchChange() {

  switchState = digitalRead(switchPin);
}

// Hardware interrupt handler for IR breaker pin 
void handleIRChange() {

  IRState = digitalRead(IRBreakerPin);  
  digitalWrite(ledPin, IRState);

}


int zeroServos() {

  servo1.attach(servo1Pin);
  servo2.attach(servo2Pin);


  for (int i = servo1Pos; i <= SERVO1_DOWN_POS; i += 1) {
      servo1.write(i);
      delay(SERVO_PULSE_DELAY);
    }   
  delay(SERVO_SETTLE_DELAY);
  servo1Pos = SERVO1_DOWN_POS;;

  for (int i = servo2Pos; i >= SERVO2_DOWN_POS; i -= 1) {
      servo2.write(i);
      delay(SERVO_PULSE_DELAY);
    }   

  delay(SERVO_SETTLE_DELAY);
  servo2Pos = SERVO2_DOWN_POS;

  servo1.detach();
  servo2.detach();
  return 0;

}

int lowerServo1(){
 
  servo1.attach(servo1Pin);
   
  for (int i = servo1Pos; i <= SERVO1_DOWN_POS; i += 1) {
      servo1.write(i);
      delay(SERVO_PULSE_DELAY);
    }   
  delay(SERVO_SETTLE_DELAY);
  servo1Pos = SERVO1_DOWN_POS;
  
  servo1.detach();
  return 0;
}

int lowerServo2(){

  servo2.attach(servo2Pin);  

  for (int i = servo2Pos; i >= SERVO2_DOWN_POS; i -= 1) {
      servo2.write(i);
      delay(SERVO_PULSE_DELAY);
    }   

  delay(SERVO_SETTLE_DELAY);
  servo2Pos = SERVO2_DOWN_POS;

  servo2.detach();
  return 0;
}



int displayPellet(whichServo side) {
  
  if(side == left){
    
    servo1.attach(servo1Pin);

    // Lower arm to grab pellet.
    for (int i = servo1Pos; i <= SERVO1_DOWN_POS; i += 1) {
      servo1.write(i);
      delay(SERVO_PULSE_DELAY);
    }   
    
    // Raise arm to display pellet
    for (int i = SERVO1_DOWN_POS; i >= SERVO1_UP_POS; i -= 1) {
      servo1.write(i);
      delay(SERVO_PULSE_DELAY);
    }
    delay(SERVO_SETTLE_DELAY);
    servo1Pos = SERVO1_UP_POS;
    servo1_up_flag = true;
    servo1.detach();
  }
  else if(side == right){
     
    servo2.attach(servo2Pin);
    // Lower arm to grab pellet.
    for (int i = servo2Pos; i >= SERVO2_DOWN_POS; i -= 1) {
      servo2.write(i);
      delay(SERVO_PULSE_DELAY);
    }   
    // Raise arm to display pellet
    for (int i = SERVO2_DOWN_POS; i <= SERVO2_UP_POS; i += 1) {
      servo2.write(i);
      delay(SERVO_PULSE_DELAY);
    }
    delay(SERVO_SETTLE_DELAY);
    servo2Pos = SERVO2_UP_POS;
    servo2_up_flag = true;
    servo2.detach();
  }

  return 0;
}



int zeroStepper() {

  digitalWrite(A3, LOW);
  for(int i = 0; i < 1000; i++)
  {
    digitalWrite(A4, HIGH);
    delay(1);
    digitalWrite(A4, LOW);
    delay(1);
  }


  digitalWrite(A3, HIGH);
  delay(100);
  
  while(!switchState){

    digitalWrite(A4, HIGH);
    delay(1);
    digitalWrite(A4, LOW);
    delay(1);
  }

  for(int i = 0; i < 50; i++)
  {
    digitalWrite(A4, HIGH);
    delay(1);
    digitalWrite(A4, LOW);
    delay(1);
  }

  stepperDistFromOrigin = 0;
  return 0;
}

int moveStepper(int targetPos) {

  int travelDist = targetPos - stepperDistFromOrigin;
  
  if(travelDist < 0){

    // If we try to move backwards but switch is pressed, set current position to origin and block movement.
    if(switchState){
      stepperDistFromOrigin = 0;
      return 2;
    }
    digitalWrite(A3, HIGH);
  }
  else{

    digitalWrite(A3, LOW);
  }
  
  int stepsToTake = abs(travelDist);
  int stepsTaken = 0;
  
  for(int i = 0; i < stepsToTake; i += 1){

    digitalWrite(A4, HIGH);
    delay(1);
    digitalWrite(A4, LOW);
    delay(1);

    if(travelDist < 0){
      
      stepperDistFromOrigin -= 1;    
    }
    else if(travelDist > 0){
      
      stepperDistFromOrigin += 1;
    }  
    stepsTaken += 1;

    // If we hit the limit switch after a short movement, we're at the origin and should abort. 
    if(stepsTaken > 1000 && switchState){

      stepperDistFromOrigin = 0;
      return 1;
    }
   
  }
  return 0;
}





void setup() {

  // Open serial connection
  // Note: This takes a bit to connect so while(!Serial) keeps it waiting
  // until the connection is ready.
  Serial.begin(9600);
  while (!Serial) {
    delay(100);
  }

  zeroServos();



  // Set switch read pin
  pinMode(switchPin, INPUT_PULLUP);
  switchState = digitalRead(switchPin);
  attachInterrupt(digitalPinToInterrupt(switchPin), handleSwitchChange, CHANGE);
  zeroStepper();

  
  // Set IR breaker read pin
  pinMode(IRBreakerPin, INPUT_PULLUP);
  IRState = digitalRead(IRBreakerPin);
  attachInterrupt(digitalPinToInterrupt(IRBreakerPin), handleIRChange, HIGH);
  // Set LED control pin
  pinMode(ledPin, OUTPUT);
  digitalWrite(ledPin, HIGH);
  pinMode(ptgreyGPIOSignalPin, OUTPUT);
  digitalWrite(ptgreyGPIOSignalPin, HIGH);
  // Let client know we're ready
  Serial.write("READY\n");
}


bool listenForStartCommand() {
  
  char authByte;
  
  while(true) {

    if(Serial.available() > 0) {
      
      authByte = Serial.read();
    }
    
    if(authByte == 'A') {

      return true;
    }
    else if (authByte == 'Y' ) {
      digitalWrite(ledPin,HIGH);
      return false;
    }

  }
}



int startSession() {

  while(!digitalRead(IRBreakerPin)) {

    char cmd;
    char stepperDist;
    
    if(Serial.available() > 0) {

      cmd = Serial.read();
      
      switch(cmd){
        
        case ('1'):
          displayPellet(right);
          break;
          
        case ('2'):
          displayPellet(left);
          break;
          
        case ('3'):

          // Give client a second to respond
          delay(1000);
          stepperDist = Serial.read();
          
          switch(stepperDist){
            case('0'):
              zeroStepper();
              break;
            case('1'):
              moveStepper(stepsToMmRatio * 1);
              break;
            case('2'):
              moveStepper(stepsToMmRatio * 2);
              break;
            case('3'):
              moveStepper(stepsToMmRatio * 3);
              break;
            case('4'):
              moveStepper(stepsToMmRatio * 4);
              break;
            case('5'):
              moveStepper(stepsToMmRatio * 5);
              break;
            case('6'):
              moveStepper(stepsToMmRatio * 6);
              break;
            default:
              break;  
            }
            
        default:
          break;
      }
    }
    
  }


  char termCmd;
  // Send session end message.
  Serial.write("TERM\n");

  if(servo1_up_flag)
  {
    lowerServo1();
    servo1_up_flag = false;
  }
  if(servo2_up_flag)
  {
    lowerServo2();
    servo2_up_flag = false;
  }
  // Flush serial buffer.
  while(Serial.read() >= 0) {
    continue;
  }

  return 0;
}



void loop() { 

  while(1){
//    /
    if(listenForStartCommand()){
      startSession();
  }
  }


  
         
}

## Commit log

2018-01-08 Merged RFID Proximity and IR into GPIO_Control.py and refactored servo control code
2018-01-10 Added camera live feed
2018-01-12 Started putting camera,RFID and servo control into their own classes.
2018-01-22 Implemented IR pressence detection, camera recording in separate process and refactored a bit.
2018-01-23 Made it so PWM signal shuts down after servo moves
2018-01-23 Fixed bugs in camera sub process and implemented PWM kill switch
2018-01-24 Moved servo-arm-cycle to it's own process and improved SessionController.startSession() accordingly
2018-01-25 Added debug logging to servo process and entered correct RFID profiles for live test
2018-03-01 Added stepper motor control for XY bed feature
2018-03-02 Improved XY bed feature and moved stepper control to long-lived process
2018-03-09 Improved comments on some files
    [Buzz Aldrin_session_history.csv, Elon Musk_session_history.csv, Jim Kirk_session_history.csv, Test Tag2_session_history.csv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]
2018-03-13 Configuring for live use
    [Buzz Aldrin_session_history.csv, Elon Musk_session_history.csv, Jim Kirk_session_history.csv, Test Tag2_session_history.csv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]
2018-03-14 Increased stepper motor speed
2018-06-06 Updating git repo with PC/Arduino/Ptgrey port
2018-06-06 Made a dependency list in the INSTALL.txt file
    [43036_MOUSE2_session_history.csv, TESTMOUSE1_session_history.csv]
2018-06-11 synced up servo movement signals after Ralph fixed servo wiring
    [43036_MOUSE2_session_history.csv, TESTMOUSE1_session_history.csv]
2018-06-20 Updated magic numbers...
    [43036_MOUSE2_session_history.csv, TESTMOUSE1_session_history.csv]
2018-07-10 Fixed camera de-initialization failure race condition
    [43036_MOUSE2_session_history.csv, TESTMOUSE1_session_history.csv]
2018-07-16 Implemented preview window for Spinnaker camera
2018-07-16 Removing camera.py because PS3 camera no longer being used
2018-07-20 Ported plotting function from RPi version to new Arduino/PC version
2018-08-13 Implemented analysis scripts for finding successful reaches in video
    [45567_MOUSE2_session_history.csv, 45567_MOUSE3_session_history.csv, 45567_MOUSE4_session_history.csv]
2018-08-15 Modified config in preparation of running v1.0
    [Test_left_session_history.csv, Test_right_session_history.csv]
2018-08-17 Modified calibration constants....need to put config in environ vars
    [Test_left_session_history.csv, Test_right_session_history.csv]
2018-09-03 Started Successful Reach vs Time graph implementation
    [45567_MOUSE2_session_history.csv, 45567_MOUSE3_session_history.csv, 45567_MOUSE4_session_history.csv, Test_left_session_history.csv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]
2018-10-31 Finished kinalyze dlc point filtering and event parsing
    [45567_MOUSE2_session_history.csv]
2018-11-21 Swapped out servo library for official Arduino one. Solves servo shooting up problem but introduces servo at-rest jitter
2018-11-21 Removed contents of AnimalProfiles directory....should not have data on github
    [45567_MOUSE2_session_history.csv, 45567_MOUSE3_session_history.csv, 45567_MOUSE4_session_history.csv, Test_left_session_history.csv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]
2018-11-21 Changed video file name format, refactored a bit
    [TEST_LEFT_session_history.csv, TEST_RIGHT_session_history.csv]
2018-11-21 TEST tags now bypass config and default to 50FPS and DisplayPreview=True
    [TEST_RIGHT_session_history.csv]
2018-11-30 Implemented bash wrapper for analyzing directories of videos with DLC and trajectory reconstruction
    [TEST_LEFT_session_history.csv, TEST_RIGHT_session_history.csv]
2018-12-12 Made servos detach after every movement (This no longer stalls with Servo.h since removing softwareserial calls). End result is no more jittering!
2019-01-15 ghetto merge
    [Flir_BlackflyS_ThorLabs_post_mount.stl, IR_ringlight_ThorLabs_post_mount.stl, baseplate.stl, beam_breaker_mount.STL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]
2019-01-15 Updated scoring GUI to prevent videos being cut off as early
2019-01-17 Refactored resources directory structure and added updated ptgrey camera post mount
    [FL2-020-R0.IGS, Flir_BlackflyS_ThorLabs_post_mount.fcstd, Flir_BlackflyS_ThorLabs_post_mount.stl, IR_ringlight_ThorLabs_post_mount.stl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]
2019-01-17 Inreased size of through holes on ptgrey camera mount
    [Flir_BlackflyS_ThorLabs_post_mount.fcstd, Flir_BlackflyS_ThorLabs_post_mount.stl]
2019-01-21 Change kinematic analysis to pad end of events with configurable number of frames
2019-01-28 A bunch of changes
    [hopper_arm_left.stl, hopper_arm_right.stl]
2019-02-06 Adding PCB enclosure CAD files
    [PCB_box.stl, PCB_lib.stl]
2019-02-08 Removed padding in scoring GUI reach videos since it's already being added at the source by kinalyze.py setting the frame indexes with padding
2019-02-25 Uploading assembly pictures
2019-02-25 Scaling all the assembly pictures to reduce size
2019-02-26 More assembly pictures
2019-03-01 Fix the calculatiion for reaching frame
2019-03-25 add the model and the tool to retrain deeplabcut and predict on new videos with it.
    [learning_stats.csv]

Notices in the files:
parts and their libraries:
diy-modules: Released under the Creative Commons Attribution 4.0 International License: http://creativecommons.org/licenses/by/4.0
